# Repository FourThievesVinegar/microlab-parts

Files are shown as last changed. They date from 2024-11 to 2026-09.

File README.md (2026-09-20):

# MicroLab 3D Printed Reactor Parts

Four Thieves Vinegar Micro Lab

This repository contains STL files for the MicroLab's 3D printed parts. The software for the MicroLab and assembly instructions can be found here: https://github.com/FourThievesVinegar/solderless-microlab.

## Reactor Versions

A fully-assembled v1.0 Microlab

### Version 7

[The v7 version](https://github.com/FourThievesVinegar/microlab-parts/tree/master/v7) includes parts for the Microlab v1.0 release.

- Updated Reactor Core with improved chemical and thermal tolerances
- Improved port placement on Pumps Box

### Version 6

The v6 version includes parts for the Microlab v0.6 release.

- New printable Control Unit case
- New printable Pumps Unit case
- New printable Reactor Box
- New printable Reactor Stand (screw-together or slot-and-tab style)
- Redesigned Reactor Manifold that includes more ports and supports stock canning jar lid rings

### Version 5
The v5 folder contains updated parts files for the Microlab v0.5 release, it adds:
- A resized motor mount (measured in mm rather than cm - look out for this in other older parts!)
- A new flange for mounting the reaction chamber in its housing

### Version 4

The v4 folder contains ~~the latest~~ old parts for the Microlab assembly, including:

- The main reactor manifold
- Lids for the heating and cooling setups
- Motor mount for the stirring motor
- Tubing adaptors
- And more! (Update me with precise file names and types)

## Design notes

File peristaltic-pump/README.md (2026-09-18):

# MicroLab Peristaltic Pump

These files are 3D part designs that can be printed and used to build an essential component of the MicroLab that can be both (1) scarce when suppliers go out of business and (2) a substantial portion of the cost of the build. It's not *done* but it *basically works*. Please feel free to fork it. If you do, let us know and we can update our docs - or maybe at that point you want to maintain your own fork of the whole project. Who knows? ;)

Status: v0.1-alpha - Interfacing with Pumps Box not yet complete. Pump itself has not been thoroughly tested or calibrated.

## What is a Peristaltic Pump?

Peristaltic pumps are a type of pump that compresses a tube using rollers. The rollers move across the surface of the tube, squeezing it and forcing small amounts of liquid through with each turn of the pump head. You know how you can get the last bits of toothpaste out of the toothpaste tube by squeezing it between your hand and the edge of your bathroom sink? It's like that.

This style of pump is named after peristalsis, which is the coordinated contractions that help move food through your intestines. Peristaltic pumps allow fluids to be pumped without ever coming into contact with the mechanical parts of the pump. The tubes can be easily replaced, which mains the pumps easy to maintain.

## Pumps in the MicroLab

The MicroLab uses a series of three pumps driven by stepper motors as part of the Pumps Box in the Reactor Unit. These pumps inject chemicals into the reaction chamber. The current designs recommended off-the-shelf peristaltic pumps but these are often hard to source. This pump is a DIY, open-source alternative. You can also use the [syringe pumps](https://github.com/FourThievesVinegar/microlab-parts/tree/master/syringe-pump) if you prefer.

## Building a MicroLab Peristaltic Pump

### The Printed Parts

First, you will need the printed parts files in the `files-STL` directory. The `images` directory contains renders of the various parts and their assembly.

### Tools

You will also need the following tools:

- soldering iron
- drill with various bits (optional but recommended)
- 2 wrenches (or a wrench with a drill with hex head attachments)

### Parts / BOM

#### Electronics

- 1x Nema17 stepper motor, 5mm shaft with fiduciary notch in shaft

#### Fasteners

- 7x M3 heat-set inserts. McMaster Carr: 94180A331 , https://www.mcmaster.com/products/heat-set-inserts/ . $20.44/100 ct
- 4x M3x32 screws (or longer)
- 4x M3x6 screws
- 3x M3x4 screws
- 6x 608 skate bearings
- 6x M8 nylock nuts
- 3x M8x? buttonhead bolt

#### Tubes
- 3/8"OD,1/8"ID latex tubing 
  - We are working on designs for tougher silicone tubes. The FreeCAD file is parameterized, so you should be able to modify the pump to work with different tube sizes if you want to.

### Preparation

#### To Begin

Print models on 3d printer. Use 30% infill or higher. Average quality settings are perfectly fine here.

#### Cleanup of printed parts

Once parts are done, carefully ream the M3, M5, and M8 holes with a drill so that the respective screws can go in without friction.

- M3 holes are the outer 4 holes, and the 4 holes connecting the stepper to the printed frame.
- M5 hole is on the bearing holder parts where the stepper shaft interfaces. (Note, if you have a 8mm stepper shaft, you can drill this part out to 8mm. Be careful and slow if you do)
- M8 holes are the bearing holder parts that hold the 608 bearings.

### Assembly

#### Stepper Base Heat-set Inserts

- Pump Base printed part
- 4x M3 heat-set inserts

On the Pump Base part, on the flat side, the outer 4 holes have a recess in them that looks like they are for a screw head. These are for heat-set inserts.
Carefully press in an insert on each outer hole of the stepper base using the tip of a hot soldering iron. To remove the soldering iron, twist while removing.
After they have cooled, remove any melted plastic debris that may have ben pushed.

#### Bearing Holder Heat-set Inserts

- Bearing Holder Bottom printed part
- 3x M3 heat-set inserts

Insert 3x M3 heat set inserts into the Bearing Holder Bottom. Carefully put on a heat-set insert on the tip of the soldering iron. Make sure the larger flat head is facing towards the soldering iron handle. Carefully press in an insert on each side of the Bearing Holder Bottom. To remove the iron, twist while gently pulling it out.
After they have cooled, remove any melted plastic debris that may have ben pushed.

#### Attach the Stepper Motor to the Pump Base

- Stepper motor
- Pump Base printed part
- 4x M3x6 screws.

Affix the stepper to the base using the M3x6 screws. Note: the M3 heat-set inserts should be on the bottom.

#### Assemble the Bearing Holder

- Bearing Holder Bottom printed part
- Bearing Holder Top printed part
- 6x 608 bearings
- 6x M8 nylock nuts
- and 3x M8x? buttonhead bolts.

Note on the 2 Bearing Holder parts: on one side there is an indentation around where the bearings will go. This is a built-in spacer to allow the bearings to freely rotate when tightened.

Put the Bearing Holder with the hexagonal shape on a table with the hex pointed up. Put the button M8 screws through it so that the screw shafts are pointing up. Then put 2x 608 bearings on each screw.

Put the Bearing Holder Top on, making sure the indentation is facing towards the bearings. Finger-tighten the nylock nuts, and then use 2 wrenches to tighten completely. The bearings should freely spin.

If the bearings do not completely spin freely, very carefully untighten the respective nylock to provide just enough room for them to spin.

#### Mounting the Bearing Holder

- Bearing Holder Assembly
- Stepper Motor + Pump Base Assembly

Place the Bearing Holder assembly on the stepper shaft. Make sure to provide a small amount of clearance at the bottom, so that the bearing holder doesnt collide with the stepper base or screws. Insert an M3x4 screw into the screw hole on the hexagonal Bearing Holder part. Align the screw with the notch in the stepper shaft. When properly tightened, it should be possible to rotate the stepper shaft by turning the Bearing Holder.

#### Completing the Assembly

- Rocker Insert printed part
- Rotating Insert printed part
- Top Plate printed part

Align the respective inserts on the screw holes. Put top plate on top. Insert a M3x32 screw through the Top Plate, Rocker Insert, and Stepper Base. Screw down to finger tight.
Align the Rotating Insert with the round groove in the Rocker Insert. Insert a M3x32 screw there and screw to finger tight.

Now, you can rock the rotating AND rocker inserts back and forth in order to easily load or change peristaltic tubing.

To close up, put the remaining screws in and tighten them.

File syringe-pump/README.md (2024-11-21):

# Microlab syringe pump

This repository contains design and 3D printable files of syringe pump used in microlab as a successor to peristaltic pumps.

## Principle of operation

Syringe pump allows to dispense arbitrary amount of fluid (limited by syringe capacity) from a syringe by pressing syringe plunge using a stepper-motor powered actuator. 

Syringe is placed in a bracket (shown in blue) and locked in place using a separate attachment (not shown in picture). 

**There is a separate bracket for each syringe diameter supported. If your syringe is slightly smaller than particular bracket it should work without problems.**

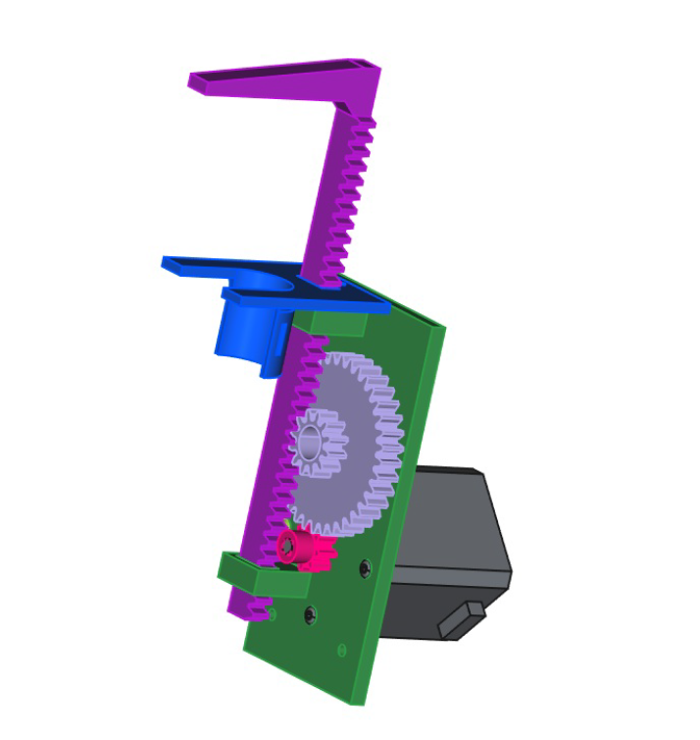
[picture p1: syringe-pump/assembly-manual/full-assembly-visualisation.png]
Syringe pump assembly visualisation


### Continuous operation

In theory such pump could operate to pump "infinite" amount of fluid by adding a valve to a syringe and using different actuator that could move syringe plunge up and down. This is not supported now but it is a possibility for the future.

## Bill of Materials

In addition to 3D printable parts from this repository, you also need:

- Nema 17 stepper motor
- 625ZZ bearing (5x16x5 mm) - it is the same bearing that is used in V-Slot/3D printer wheels.
- 4 x M3x6 pan head hex screws for mounting Nema 17 motor (ISO 7380)
- M5x20 pan head hex screw and nut (ISO 7380)
- M3x20 screw and nut (type does not matter)

## 3D printing considerations

Although not mandatory - we highly recommend proper tuning of your 3D printer flow and dimension accuracy.

### Material
Both PLA and PETG were tested and are sufficient.

### Slicing

Below recommended printing settings apply to Cura slicer - other slicers may use different names for those settings.

- Layer height: 0.2 mm
- Perimeters (walls): at least 5 for gears and syringe actuator
- Infill: 20% or more
- Cooling: try at least 40-60% when printing base plate (unless you have no problems with printing overhangs)

### Supports
Supports are needed for printing the base plate. 

If there is too much  sag on a motor pad overhangs there may be problems with proper motor alignment. If you struggle to get good supports (as most people do) here are Cura settings worth trying:

- Support density: 15%
- Support Z Distance: 0.2 mm
- Support X/Y distance: 1.5 mm
- Enable support interface: Checked
- Enable support roof: Checked (may not show in slicer, don't worry)
- Support interface density: 15%
- Support interface pattern: Zig-Zag (this is most important setting!!)

## Assembly instructions

### 1 - Insert bearing into conversion gear

You may need to use some force, there are special crush-ribs designed in the hole to deform while inserting the bearing to hold it tight. Make sure bearing is placed evenly.

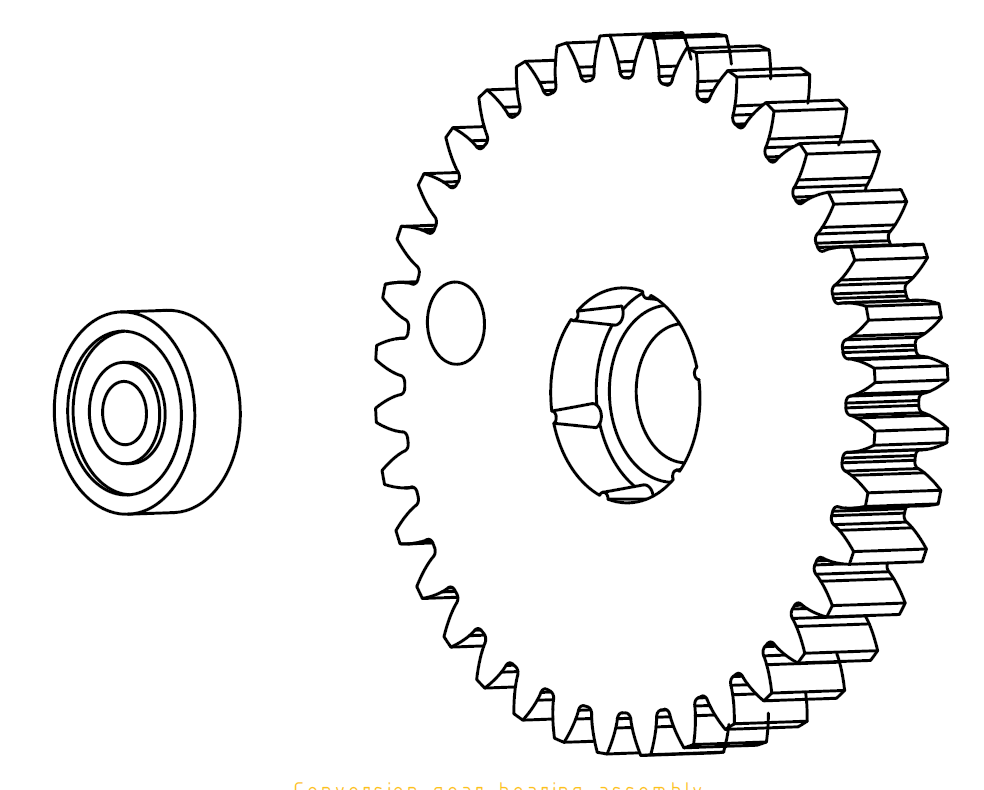
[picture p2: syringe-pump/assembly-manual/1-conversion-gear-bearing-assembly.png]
Conversion gear bearing mount


### 2 - Screw motor to the back plate

Use M3x6 screws.

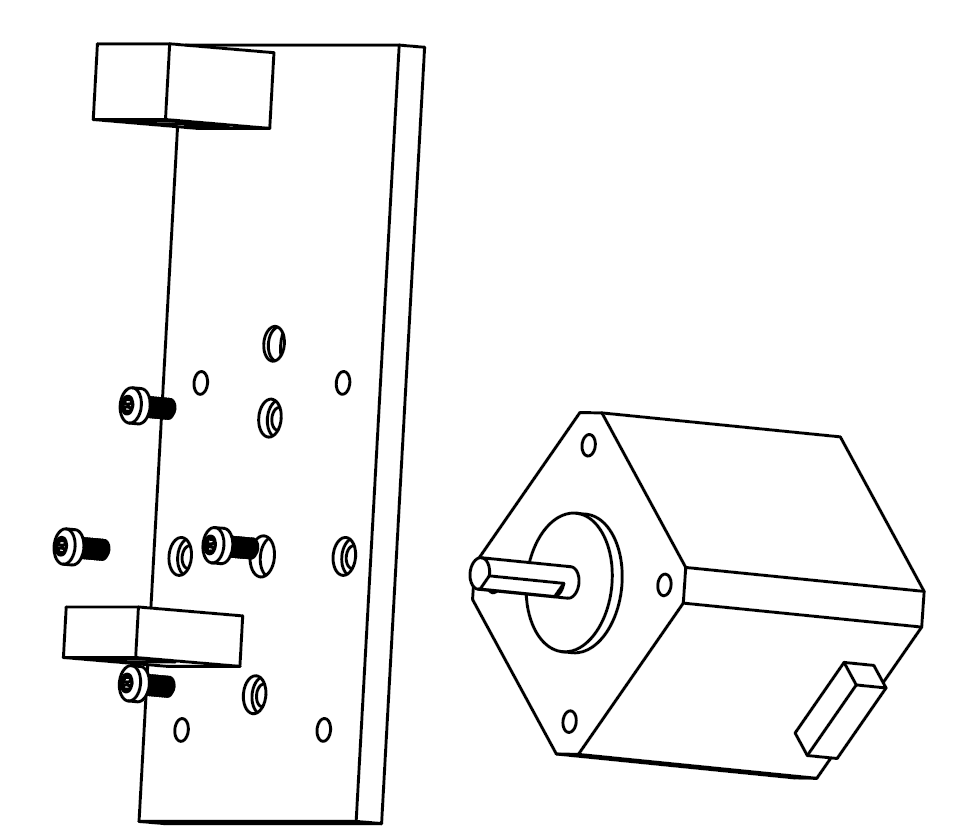
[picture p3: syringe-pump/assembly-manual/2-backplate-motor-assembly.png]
Back plate motor assembly


### 3 - Attach conversion gear to the back plate

Use M5x20 screw and nut. You will most likely need to hold the nut in place using small pliers or a screwdriver while tighening the screw. 

If the bearing does not sit evenly in the gear, the gear may not rotate freely and grind on the plate - you need to realign the bearing then. In some rare cases, like out of spec bearing, you may need to add a M5 washer between bearing and the plate to rise the gear a little.

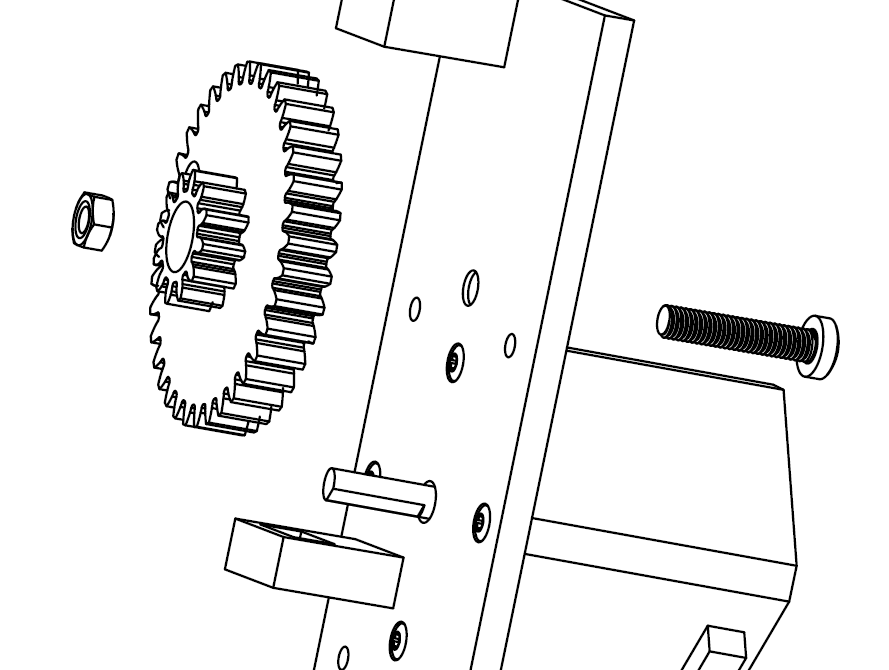
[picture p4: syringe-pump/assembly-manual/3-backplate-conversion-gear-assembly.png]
Conversion gear back plate assembly


### 4 - Attach motor gear

Insert smaller gear onto motor shaft. You may also need to use some amount of force.
Please note that there is only one position where gear hole matches the shaft shape.

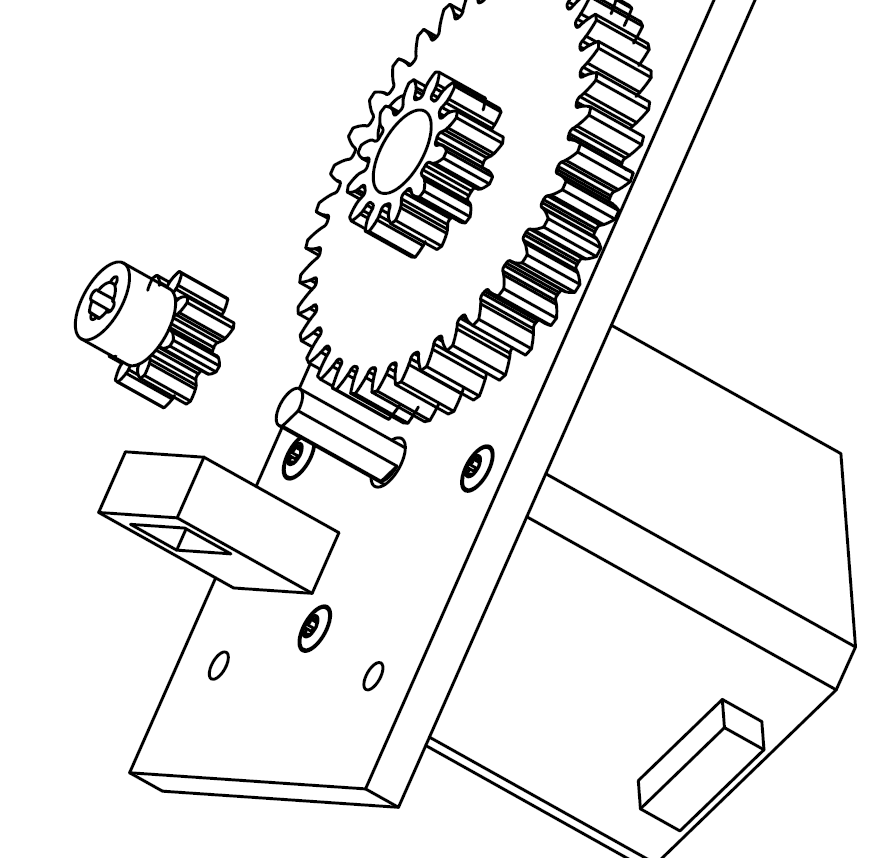
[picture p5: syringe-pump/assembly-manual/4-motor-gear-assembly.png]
Motor gear assembly


### 5 - Attach syringe bracket

Attach syringe bracket using M3x20 screw and nut.

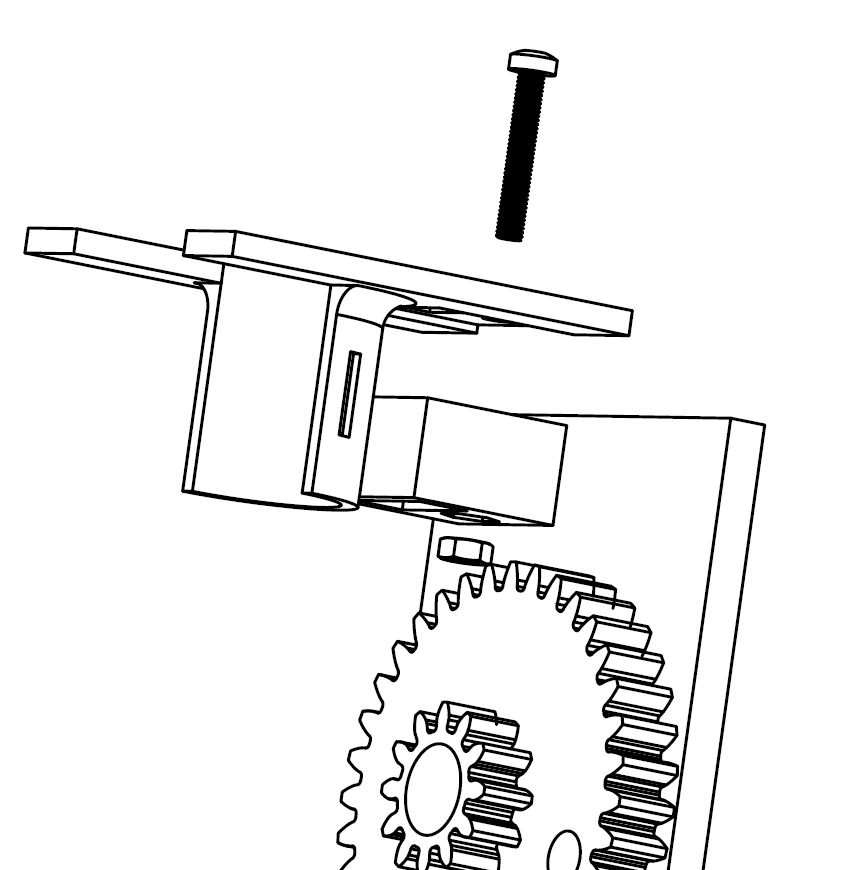
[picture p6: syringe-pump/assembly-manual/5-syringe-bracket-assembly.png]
Syringe bracket assembly


### 6 - Attach syringe actuator

Insert syringe actuator through both guide holes.

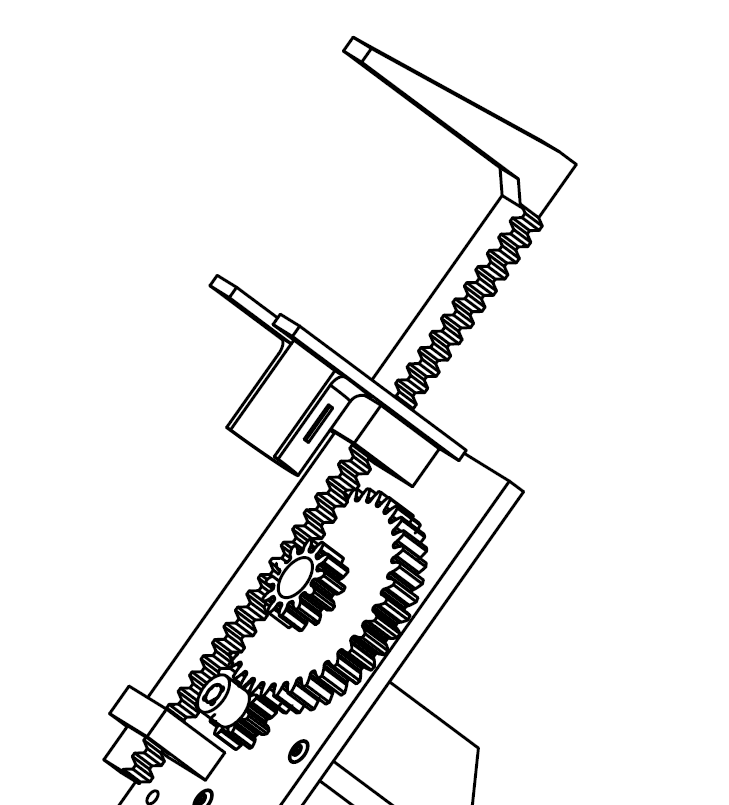
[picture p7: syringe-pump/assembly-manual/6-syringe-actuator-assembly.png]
Syringe actuator assembly


## Custom syringe diameter support

If you need syringe bracket with diameter not supported by available files, you can easily generate it yourself using FreeCAD.

Open design file with FreeCAD, go to syringe bracket object. Syringe bracket is parametric - just set desired diameter in "Config" varset, wait till object regenerates and export it to STL/STEP file.

## FAQ

### Motor is too weak to press a syringe plunge.
Make sure pump is not locked - by manually rotating small gear. 

Do it when motor is disabled from power - depending on controller, motor may be activated all the time, even when not moving - and making it impossible to rotate by hand.

Possible causes why motor may be too weak:
- Stepper motor driver uses so called "microstepping" which makes motor more silent and precise. Microstepping reduces motor torque. Try disabling microstepping or at least reducing the microstep ratio.
- Too small motor current. Check motor and motor driver datasheets to verify the maximum current they can handle. If possible, increase motor current as it will increase the torque.
- Compare your motor's model datasheet specification (torque) with other Nema 17 motor models. If your model has abnormally lower torque than other models, it may be the case.
- Try reducing motor speed while pumping

As experiments show - 17HS4401 motor running at 1A current has enough torque to easily move a syringe plunge at wide range of speeds.

### Pump damages itself or syringe when pumping beyond end of syringe capacity

Pump is designed and tested to not do any damage when pumping beyond syringe capacity. Motor is expected to stop moving and start skipping steps when there is no way to move gears.

**If syringe bracket is breaking, try printing it with larger infill percentage and more top/bottom layers.**

If motor torque is too large and causes locked pump or syringe to be damaged, try lowering motor current by reconfiguring stepper motor driver. Refer to motor and driver data sheets for safe current ratings. Running motor **below** its nominal current specified in datasheet is perfectly fine.

**This pump was only tested with plastic syringes. You are using glass syringes at your own risk (as everything else here anyway).**

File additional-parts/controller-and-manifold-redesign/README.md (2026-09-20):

# Alternate Control Box and Reactor Manifold Design

These files were sent to us by an independent replicator. We have not tested or vetted them, but the included media shows how it works and fits together. It is based on the v0.6.0 designs and the photos include some parts that are no longer needed, like the switchable IOT power plug.

We are including it here for posterity so that others can experiment and continue to remix the project.

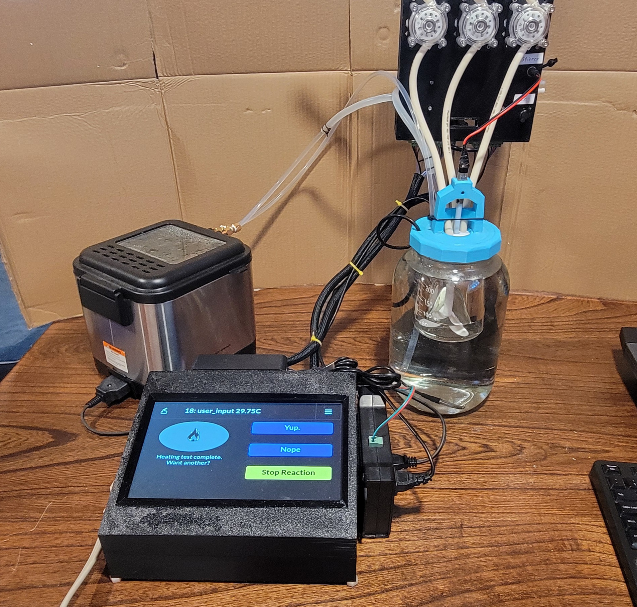
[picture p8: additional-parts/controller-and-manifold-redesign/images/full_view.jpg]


## Alternate Components

- Display: [ROADOM 10.1" Touchscreen Monitor, 1024x600 IPS Raspberry Pi Screen, HDMI](https://www.amazon.com/dp/B09XDK2FRR?th=1)
- Outer jar: larger 1/2 gallon mason jar

## Alternate Assembly Info

### The Control Box

The screen mounts into the case with M3 screws. All the components (arduino with pump controllers, 5v regulator and relays module) all mount to standoff posts using M3 screw so everything stays in place and doesn't use snap tabs that often break when 3D printed. The two halves of the case use 4 M4x50mm screws to hold them together; the holes for the screw heads weren't quite big enough but you can use some M4 rubber feet. The design also might need some extra vent holes if the pump controllers get too hot, possibly with a small computer fan for circulation. The design also adds strips of velcro to the 12V power supply and IOT plug (IOT plug shown in images is not needed for the 1.0 MicroLab) so everything is held together as one solid unit.

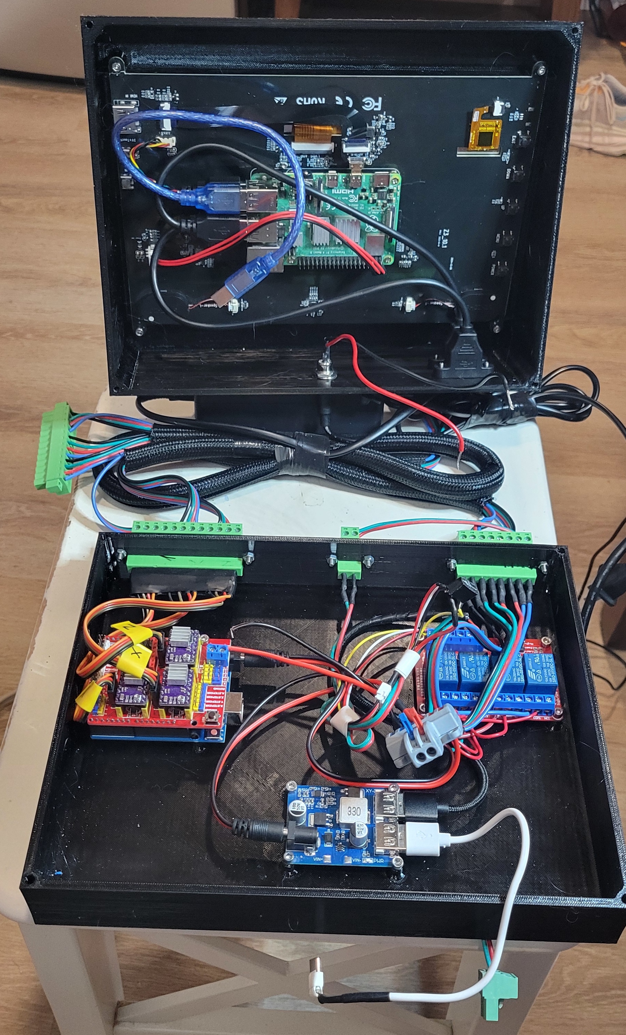
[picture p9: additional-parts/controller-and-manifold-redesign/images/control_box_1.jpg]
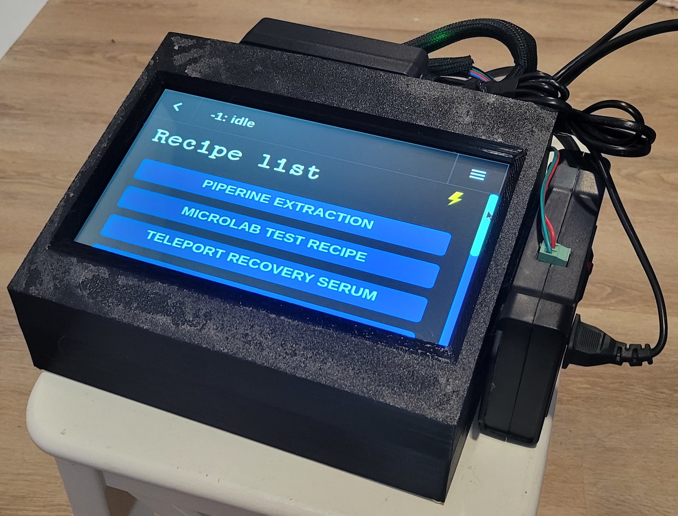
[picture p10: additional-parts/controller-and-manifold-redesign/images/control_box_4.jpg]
 

### The Manifold

The manifold design is a tweaked version of the GL45 manifold with some extra changes - it adds a flange on the edges of the manifold where it sits on the top of the jar and has a better rim that screws onto the mason jar. It also changes where the motor sits to be much more snug. The thermometer wire goes through a slanted hole right on the edge of the lid (this may require reaming the hole with a drill but it fits great). The design also makes the circulation pipe holes big enough that they can fit 5.5mm silicone grommets (8mm drill hole).

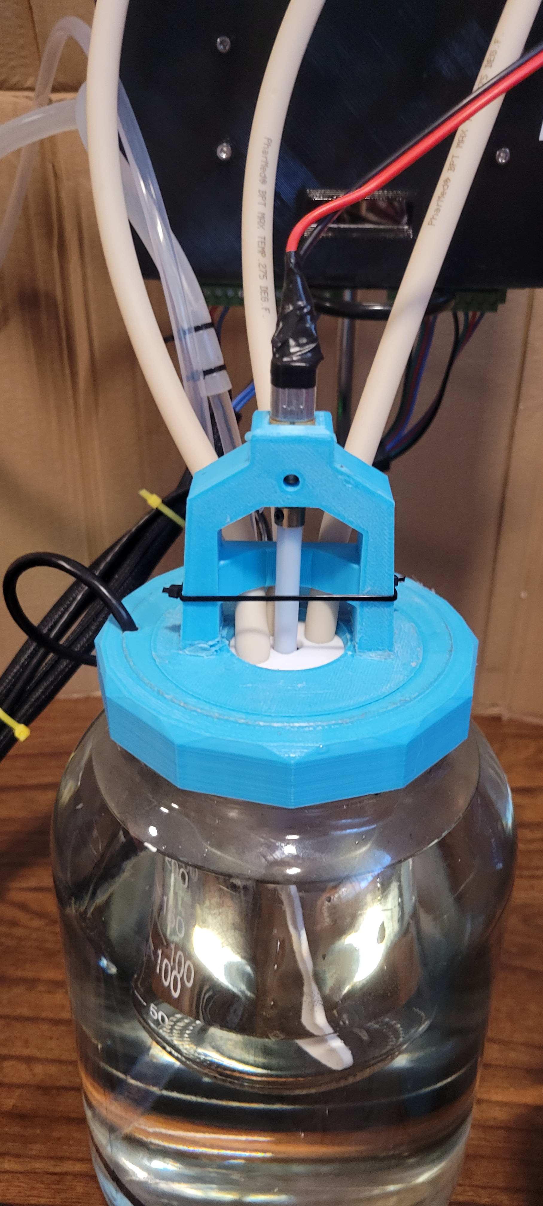
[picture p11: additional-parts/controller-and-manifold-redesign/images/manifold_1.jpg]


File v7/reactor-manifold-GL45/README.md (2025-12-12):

# GL45 Variant Reactor Core

This design uses a borosilicate media bottle with GL45 threads as the inner vessel and a hand-cut teflon disk as the lid to improve chemical compatibility. Because the sealing surface is the bottom of the teflon disk, not the edges, tight tolerances are not required.

## Parts

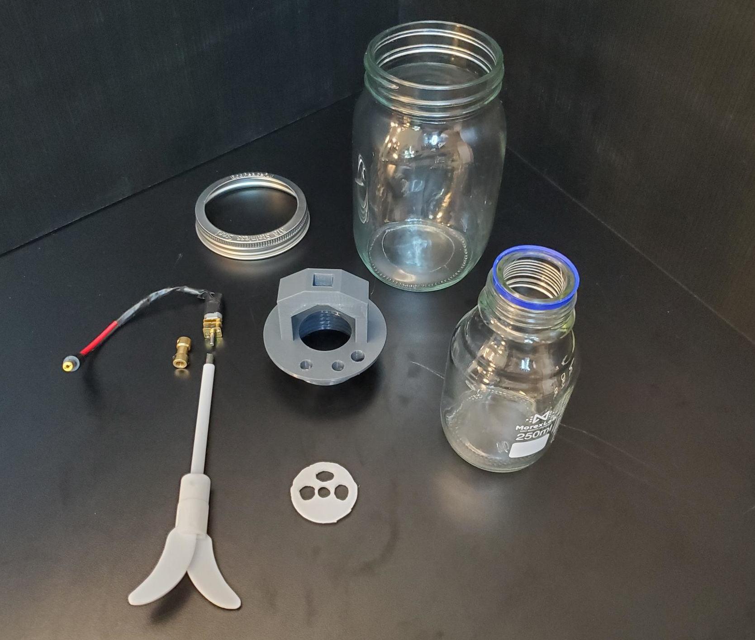
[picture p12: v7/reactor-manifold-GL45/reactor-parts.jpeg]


Reactor Core parts list:

- Outer Jar and lid ring
- Inner 250ml GL45 borosilicate bottle
- Printed Reactor Core
- Carved PTFE Disc
- PTFE stirrer
- Shaft coupler.
- Motor with barrel plug attached

Refer to [the parts list](https://github.com/FourThievesVinegar/solderless-microlab/raw/refs/heads/main/docs/microlab-parts-list.xlsx) for exact specifications and notes.

## PTFE Disc

The disc itself is approximately 35mm in diameter. The stirrer in the parts list requires a central hole approximately 8mm in diameter. The reagent pump tubes have an outside diameter of 10mm. While it is possible to drill PTFE, it is much easier to work it with a knife.

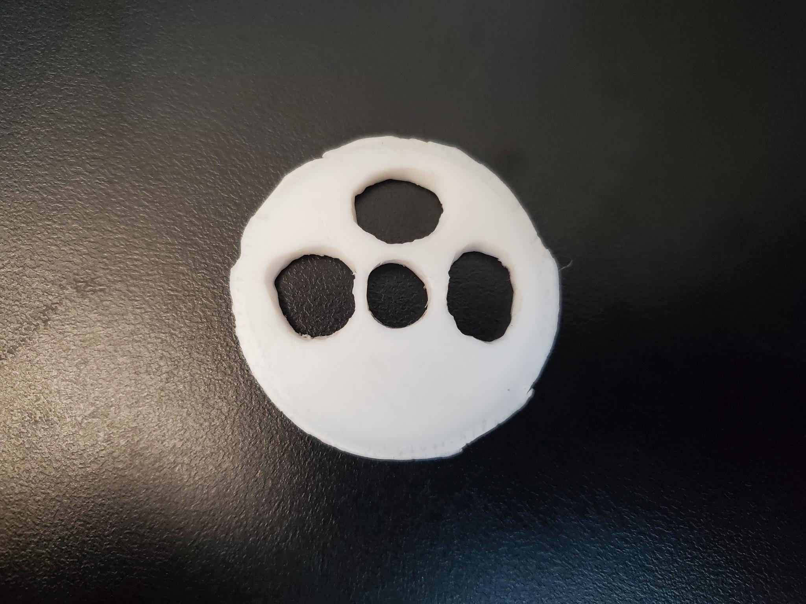
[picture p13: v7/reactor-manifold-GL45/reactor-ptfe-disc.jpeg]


## Assembled

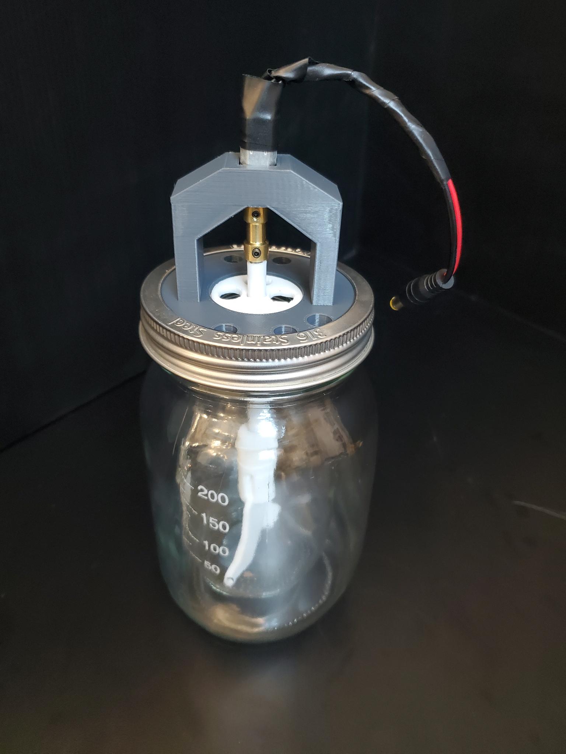
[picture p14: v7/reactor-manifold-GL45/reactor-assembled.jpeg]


## Increasing Temperature Tolerance

The temperature tolerance of the Reactor Core is a major reason for the transition to this new design. In order to increase tolerances further, we have conducted annealing experiments involving heat treating the part. Based on these experiments, we recommend the following:

- Print the part in PETG filament, which has more thermal resistance than PLA. If you have used other materials, and especially if you have conducted temperature tests, please contact us with your findings. 
- Anneal the PETG manifold in an oven for 60 minutes at 185°F / 85°C.
- This will cause the part to shrink in the X/Y dimensions and expand slightly in the Z direction. To account for this deformation, we recommend scaling the model to 103.5% in the X and Y dimensions while scaling it to 97.5% in the Z dimension.

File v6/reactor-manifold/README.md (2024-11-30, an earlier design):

### Manifold core

Manifold core comes in 2 versions - regular and split. Split one consists of two parts (top and bottom) which can be printed separatedly and glued.

For some people it may be more handy and faster than printing reguar core which requires large supports 
(you would still need small supports for screw nut pockets).

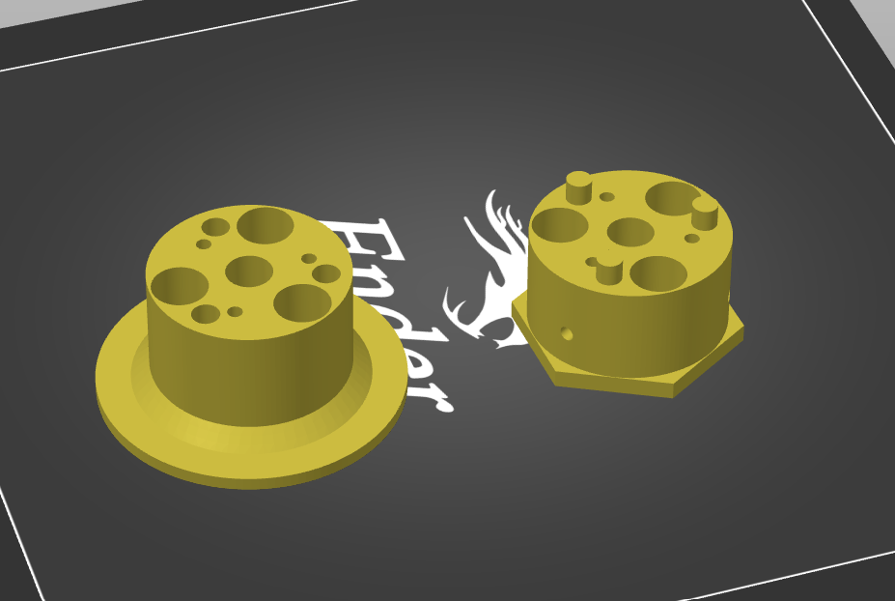
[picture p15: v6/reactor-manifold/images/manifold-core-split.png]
split core


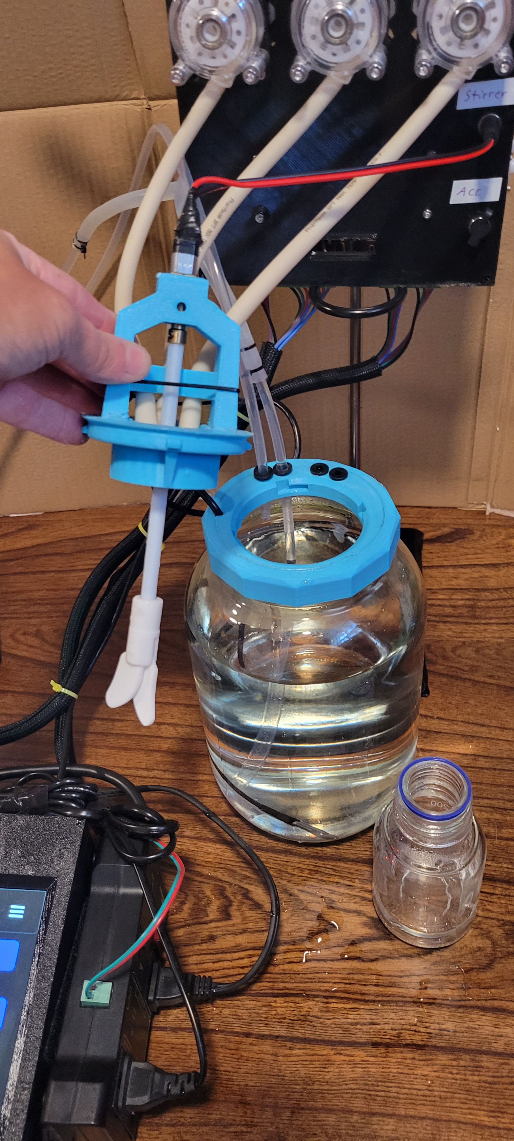
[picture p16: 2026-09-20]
additional-parts/controller-and-manifold-redesign/images/manifold_4.jpg

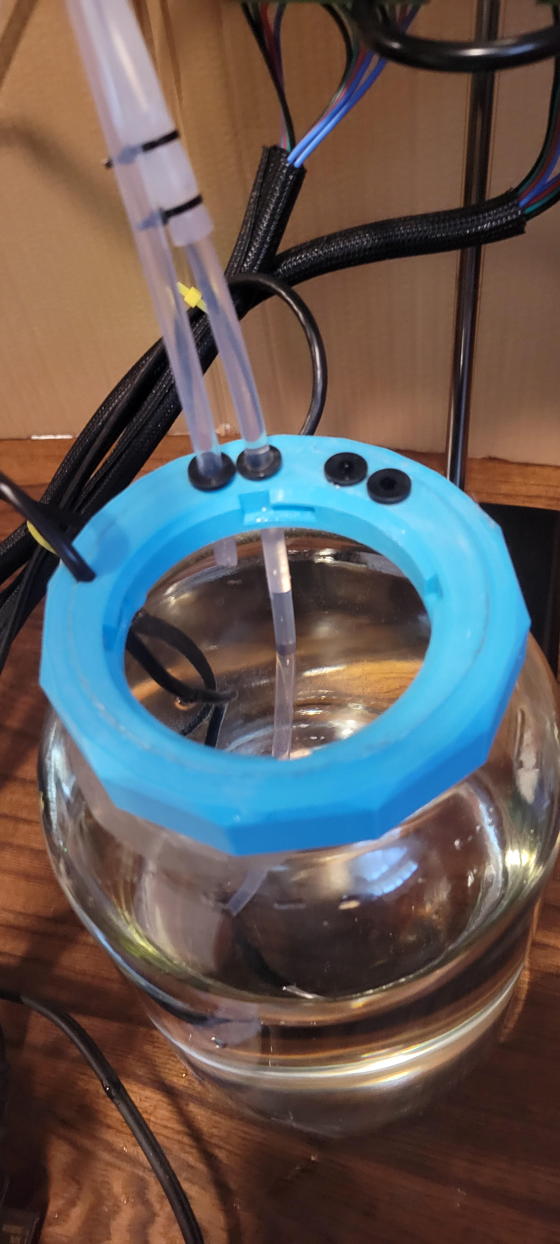
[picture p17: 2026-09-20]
additional-parts/controller-and-manifold-redesign/images/manifold_2.jpg

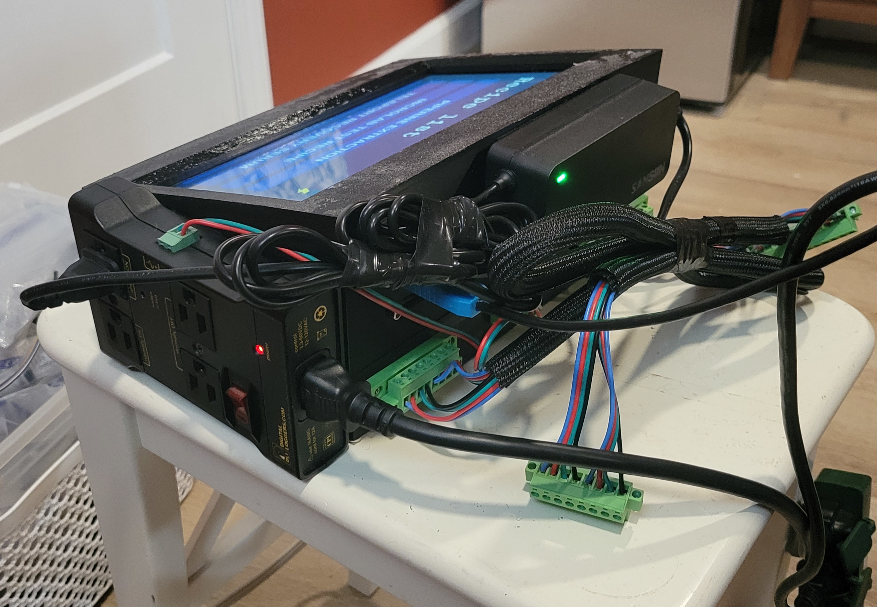
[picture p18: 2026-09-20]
additional-parts/controller-and-manifold-redesign/images/control_box_3.jpg

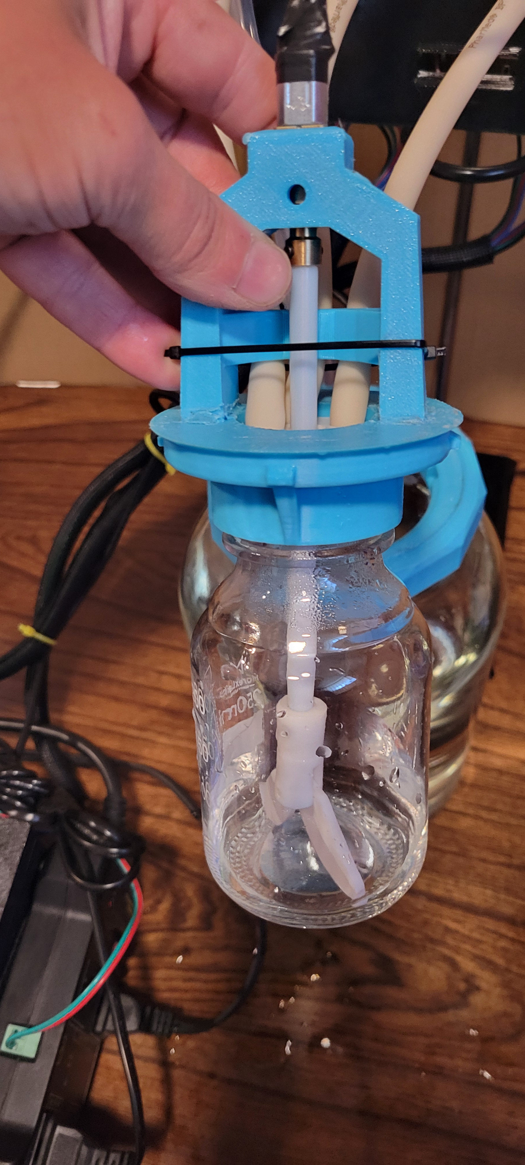
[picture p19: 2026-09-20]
additional-parts/controller-and-manifold-redesign/images/manifold_3.jpg

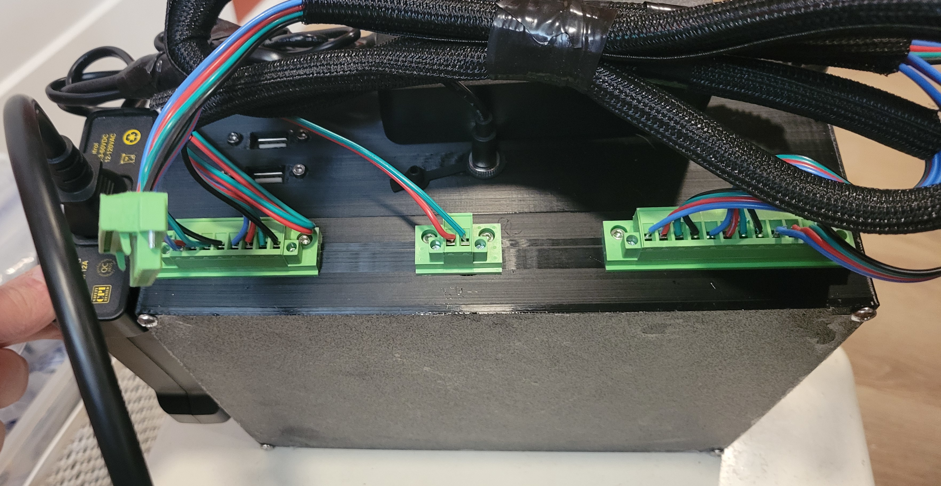
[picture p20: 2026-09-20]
additional-parts/controller-and-manifold-redesign/images/control_box_2.jpg

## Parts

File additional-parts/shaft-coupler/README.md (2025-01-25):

# Stir Shaft Coupler

A printable shaft coupler to connect the Reactor Core's stirring paddle rod to the stirrer motor.

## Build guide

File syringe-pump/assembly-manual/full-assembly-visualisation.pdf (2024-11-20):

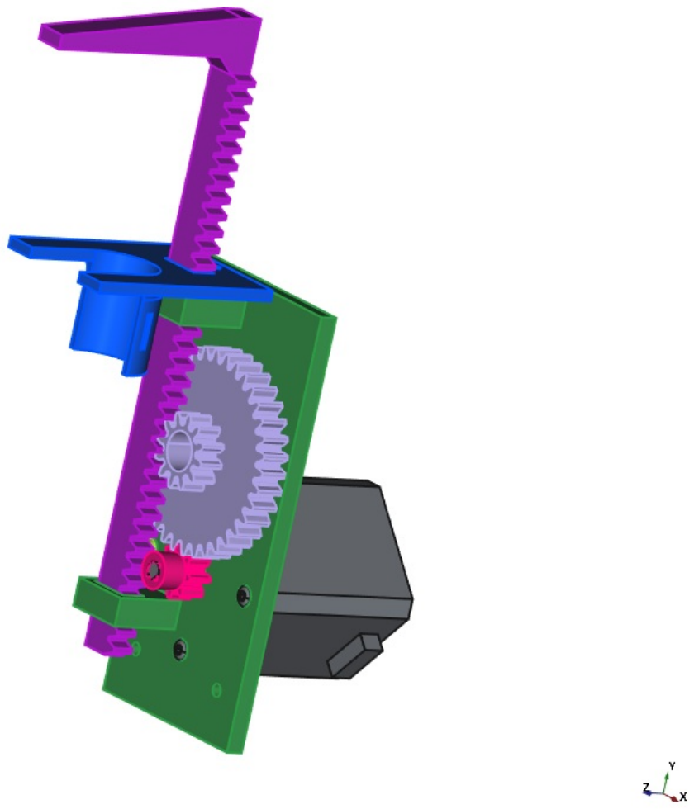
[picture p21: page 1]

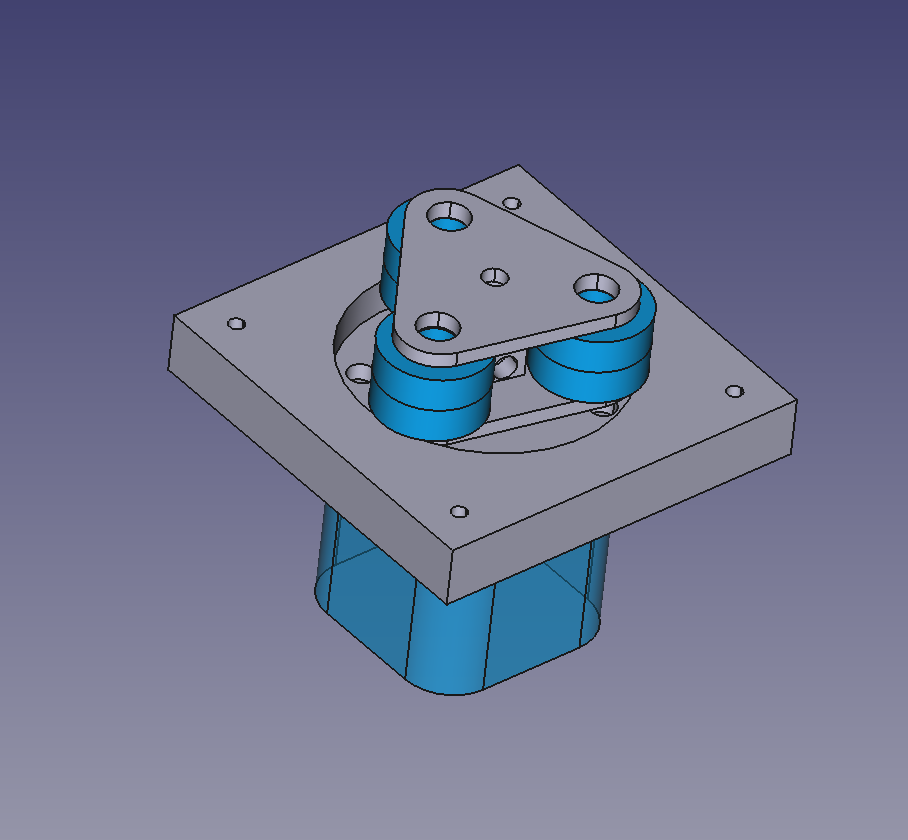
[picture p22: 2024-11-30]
peristaltic-pump/images/stepper assembly with bearing assembly.png

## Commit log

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2018-09-10 Add files via upload
    Designed to be adjustable depending on the size of the spacer, but for standardized mason jar mouth sizes.
    **Please print with the most chemically resistant polymers available. Please source Stainless Steel fasteners for best results. Additional parts on the way..
    [2in 6-32 stainless steel screw.stl, 6-32 stainless steel nut.stl, bottom.stl, qtrIN -18NPT barbed hose fitting 5361K360_TYPE 304 STAINLESS STEEL BARBED HOSE FI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]
2018-09-10 create directory for VON HIPPEL REACTOR v0.5
    [2in 6-32 stainless steel screw.stl, 6-32 stainless steel nut.stl, bottom.stl, qtrIN -18NPT barbed hose fitting 5361K360_TYPE 304 STAINLESS STEEL BARBED HOSE FI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]
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2022-08-28 check in v4 part files
    [2in 6-32 stainless steel screw.stl, 6-32 stainless steel nut.stl, 800ml to 150ml adapter bottom 2.stl, 800ml to 150ml adapter top 2.stl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]
2022-11-03 replace old reactor file
    [2in 6-32 stainless steel screw.stl, 6-32 stainless steel nut.stl, 800ml to 150ml adapter bottom 2.stl, 800ml to 150ml adapter top 2.stl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]
2023-10-03 new parts and v5 directory
    [jar flange.STEP, jar flange.STL]
2024-01-06 Re-Cad'ed stirring mount files.
    [stirringMount.step, stirringMount.stl]
2024-01-22 Rename stirring mount.stl to stirring mount(outdated).stl
    [stirring mount(outdated).stl]
2024-01-22 Updated CAD files for hot masonjar
    [hotMason.step, hotMason.stl]
2024-01-22 Updated CAD files for cold mason jar
    [coldMason.step, coldMason.stl]
2024-01-22 rename files and remove old stirring mount
    [jarFlange.STEP, jarFlange.STL, stirring mount(outdated).stl]
2024-01-22 Uploading new reactor manifold STEP file
    [reactorManifold_v0.7.step]
2024-04-22 new v0.6 printable parts
    [control-box-lid-v0.2.step, control-box-lid-v0.2.stl, control-box-v.0.5.step, control-box-v.0.5.stl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]
2024-04-22 Add the jar flange to v0.6
    [reactor-stand-jar-flange.v0.1.STEP, reactor-stand-jar-flange.v0.1.STL]
2024-04-25 align coupling of core manifold and core lid
    [reactor-manifold-core-v0.1.step, reactor-manifold-core-v0.1.stl]
2024-04-27 Add vent holes to control box
    [reactor-box-v.0.7.step, reactor-box-v.0.7.stl]
2024-05-04 update control box and lid
    [control-box-lid-v.1.0.FCStd, control-box-lid-v.1.0.step, control-box-lid-v.1.0.stl, control-box-lid-v0.2.step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]
2024-05-04 Add gitignore and tweak control-box
    [control-box-v.1.1.FCStd, control-box-v.1.1.step, control-box-v.1.1.stl]
2024-05-05 Tweak control box and make lid slightly longer
    [control-box-lid-v.1.0.FCStd, control-box-lid-v.1.0.step, control-box-lid-v.1.0.stl, control-box-v.1.1.FCStd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]
2024-05-06 Tweak lid size and rear cut placement
    [control-box-lid-v.1.0.FCStd, control-box-lid-v.1.0.step, control-box-lid-v.1.0.stl, control-box-v.1.1.FCStd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]
2024-05-08 Fix missing control box stl
    [control-box-v.1.1.stl]
2024-05-09 Add original CAD files and temp control parts.
    [cold-unit-lid-v.1.0.step, cold-unit-lid-v.1.0.stl, hot-unit-lid-v.1.0.step, hot-unit-lid-v.1.0.stl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]
2024-05-11 Tweak hot lid heater catch
    [hot-unit-lid-v.1.0.step, hot-unit-lid-v.1.0.stl, temperature-control-units-lids.FCStd]
2024-05-14 Let's call these "good enough for release"
    [cold-unit-lid-v.1.0.step, cold-unit-lid-v.1.0.stl, control-box-lid-v.1.0.FCStd, control-box-lid-v.1.0.step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]
2024-05-21 Rename "reactor box" to match naming elsewhere
    [pumps-box-lid-v0.3.step, pumps-box-lid-v0.3.stl, pumps-box-v.0.7.step, pumps-box-v.0.7.stl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]
2024-05-25 Control box tweaks, new stepdown case, fix pumps box step file
    [control-box-v.1.1.FCStd, control-box-v.1.1.step, control-box-v.1.1.stl, pumps-box-v.0.7.step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]
2024-05-27 Fix pumps box exports and Control Unit sub-cases.
    [pumps-box-v.0.7.step, pumps-box-v.0.7.stl, relay-board-case-50x73x17mm-Relay Case With Anchor.step, relay-board-case-50x73x17mm-Relay Case With Anchor.stl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]
2024-06-07 Updates for v0.6 release candidate parts
    [control-box-flat-v.1.0.FCStd, control-box-flat-v.1.0.step, control-box-flat-v.1.0.stl, control-box-lid-flat-v.1.0.step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]
2024-06-13 More control box sub-components, tweaked stand, tweaked pumps box, cut files for lids
    [control-box-flat-v.1.0.step, control-box-flat-v.1.0.stl, control-box-lid-flat-v1.0.dxf, pumps-box-lid-v0.3.FCStd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]
2024-06-19 More control box lid screen cut tweaks
    [control-box-lid-flat-v.1.0.step, control-box-lid-flat-v.1.0.stl, control-box-lid-flat-v1.0.dxf]
2024-06-20 More flat control box lid tweaks
    [control-box-lid-flat-v.1.0.step, control-box-lid-flat-v.1.0.stl, control-box-lid-flat-v1.0.dxf]
2024-06-20 Tweak Pumps Box plug locations and move old screw-together version to sub-folder
    [pumps-box-v.0.7.step, pumps-box-v.0.7.stl, pumps-box-v.1.0.step, pumps-box-v.1.0.stl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]
2024-07-01 Update reactor-stand file with pumps box export. Fix step down and relay board cases.
    [reactor-stand-1.0.FCStd, relay-board-case-50x73x17mm-no-top.FCStd, relay-board-case-50x73x17mm-no-top.step, relay-board-case-50x73x17mm-no-top.stl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]
2024-07-08 Added pumps box, steppers, syringes
    [reactor-stand-1.0.FCStd]
2024-07-24 Add slot for 8mm/16mm bearing in the manifold core
    [reactor-manifold-core-v0.1.FCStd, reactor-manifold-core-v0.1.step, reactor-manifold-core-v0.1.stl]
2024-07-24 Add a chamfer to better support the reaction chamber lid
    [reactor-manifold-core-v0.1.FCStd, reactor-manifold-core-v0.1.step, reactor-manifold-core-v0.1.stl]
2024-09-16 Fix missing control-box-lid stl, push minor control-box-flat updates.
    [control-box-flat-v.1.0.FCStd, control-box-flat-v.1.0.step, control-box-flat-v.1.0.stl, control-box-lid-v.1.0.stl]
2024-09-18 Chamfer manifold core to avoid using supports during print
    [reactor-manifold-core-v0.1.FCStd, reactor-manifold-core-v0.1.step, reactor-manifold-core-v0.1.stl, reactor-manifold-core-v0.2.FCStd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]
2024-10-24 Revert "Chamfer manifold core to avoid using supports during print"
    This reverts commit 8e6bc8d3e1338ca2aba29d7a3cd89e59021f9e26.
    [reactor-manifold-core-v0.1.FCStd, reactor-manifold-core-v0.1.step, reactor-manifold-core-v0.1.stl, reactor-manifold-core-v0.2.FCStd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]
2024-11-08 Manifold core split for printing and glueing
    [reactor-manifold-core-split-v0.1-Bottom.step, reactor-manifold-core-split-v0.1-Bottom.stl, reactor-manifold-core-split-v0.1-Top.step, reactor-manifold-core-spl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]
2024-11-18 add assembly manual + FC assemblies
    [assembly-parts.FCStd, back-plate.step, back-plate.stl, syringe-pump-assembly.FCStd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]
2024-11-19 stl/step files, readme update
    [conversion-gear.step, conversion-gear.stl, motor-gear.step, motor-gear.stl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]
2024-11-26 Add missing screw pads for pump box mount
    [back-plate.step, back-plate.stl, syringe-bracket-21mm.stl, syringe-pump-v2.FCStd]
2024-11-26 Increase back plate thickness
    [back-plate.step, back-plate.stl, syringe-pump-v2.FCStd]
2024-11-30 Add Peristaltic pumps files
    [bearing holder bottom.stl, bearing holder top.stl, peristaltic-pump.FCStd, pump base.stl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]
2024-12-30 Add correct screw-together c part
    [reactor-stand-c.v0.1.stl]
2025-01-25 Add "Eight Hands" reactor manifold files
    [reactor-manifold-eight-hands.FCStd, reactor-manifold-eight-hands.step, reactor-manifold-eight-hands.stl]
2025-01-25 Add stir shaft coupler
    [stir-shaft-coupler.FCStd, stir-shaft-coupler.step, stir-shaft-coupler.stl]
2025-01-25 Rename some files
    [reactor-manifold-GL45.FCStd, reactor-manifold-GL45.step, reactor-manifold-GL45.stl, stir-shaft-coupler.FCStd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]
2025-06-16 Update Control Box Lid tabs
    [control-box-lid-flat-v.1.0.step, control-box-lid-flat-v.1.0.stl]
2025-06-16 Add additional experimental peristaltic pump design
    [peristaltic-housing-bottom.FCStd, peristaltic-housing-top.FCStd, peristaltic-rotor-bottom.FCStd, peristaltic-rotor-top.FCStd]
2025-06-18 Tweak Control Box lid tabs
    [control-box-lid-flat-v.1.0.step, control-box-lid-flat-v.1.0.stl]
2025-06-22 Improved Pumps Box design. No-connectors Lid.
    [pumps-box-lid-v0.4-no-connectors.FCStd, pumps-box-lid-v0.4-no-connectors.step, pumps-box-lid-v0.4-no-connectors.stl, pumps-box-v.1.0.step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]
2025-09-07 fix: Clean up pumps box file, make barrel plug holes larger.
    [pumps-box-v.1.1.step, pumps-box-v.1.1.stl, pumps-box-v1.1.FCStd]
2025-09-16 Bumped compatability to FreeCAD 1.0
    [reactor-stand-A.v0.2.FCStd, reactor-stand-H.v0.2.FCStd, reactor-stand-c.v0.2.FCStd, reactor-stand-k.v0.2.FCStd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]
2025-09-18 add hole for temperature probe
    [reactor-manifold-GL45-Cut001.step, reactor-manifold-GL45.FCStd]
2025-09-18 fix file names
    [reactor-manifold-GL45-Cut001.step, reactor-manifold-GL45.step]
2025-09-19 Update images and GL45 reactor core docs, rearrange files,
    [reactor-manifold-GL45.FCStd, reactor-manifold-GL45.step, reactor-manifold-core-split-v0.1-Bottom.step, reactor-manifold-core-split-v0.1-Bottom.stl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]
2025-10-07 add v7 parts (for MicroLab 1.0)
    [cold-unit-lid-v.1.0.step, cold-unit-lid-v.1.0.stl, control-box-lid-v.1.1.step, control-box-lid-v.1.1.stl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]
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
